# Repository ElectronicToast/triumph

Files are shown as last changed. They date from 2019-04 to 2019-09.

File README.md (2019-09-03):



  

Analog function generator project for EE 90 at Caltech

## Description

The Triumph Analog Function Generator is an analog function generator constructed for the Analog Electronics Project Laboratory (EE 90) capstone course at Caltech. It provides a single output channel on a 50 Ω impedance matched BNC connector. It is capable of producing sine, square, and triangle waveforms that vary in frequency over at least the range 10 Hz to 20 kHz, in addition to DC. The frequency may be adjusted through the combination of a frequency range select switch and a fine-adjustment knob on the top of the device. The output amplitude may be varied from zero up to 10 V (single-sided)  with a control knob. A second control knob allows the DC offset of the output to be varied. 

Power is supplied via 9 – 18 VDC input through a barrel jack connector on the rear of the device. A rocker switch near the power connector allows the device to be switched on and off.

A blue indicator LED on the front of the device indicates if the function generator is powered.

## Photos

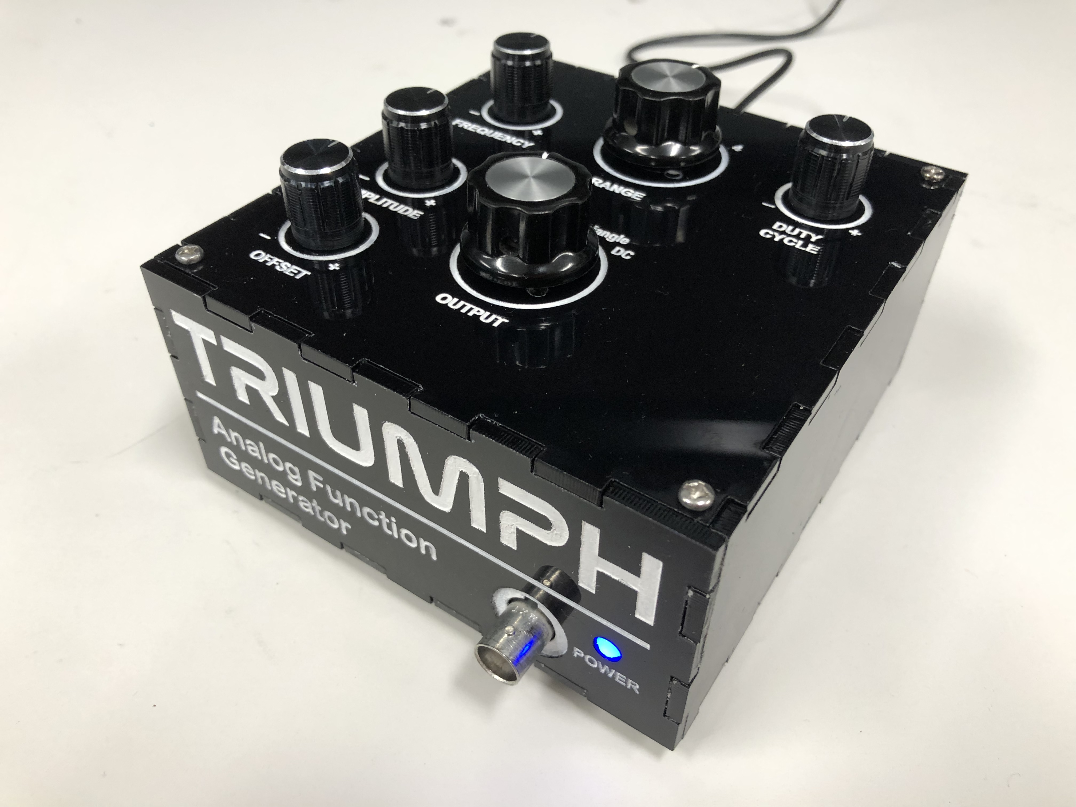
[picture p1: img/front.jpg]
front

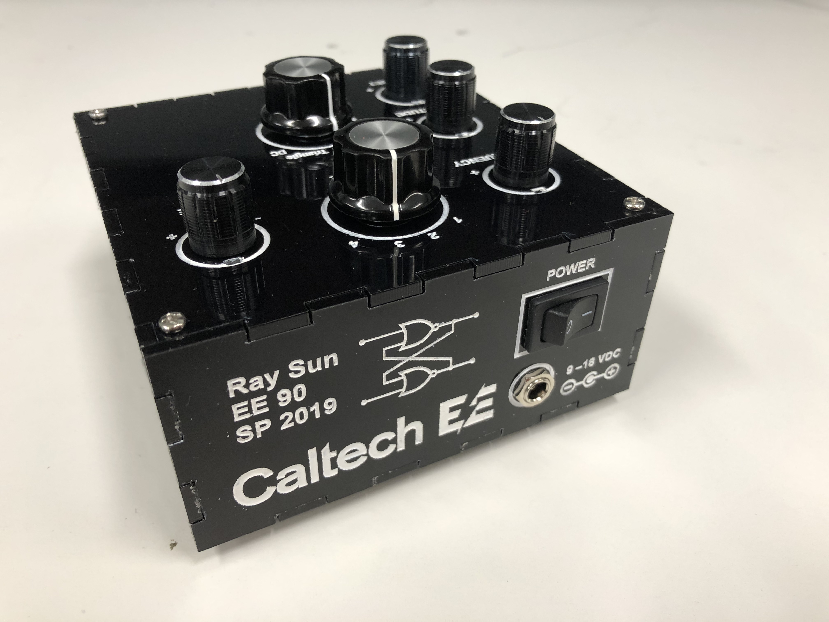
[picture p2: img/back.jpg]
back

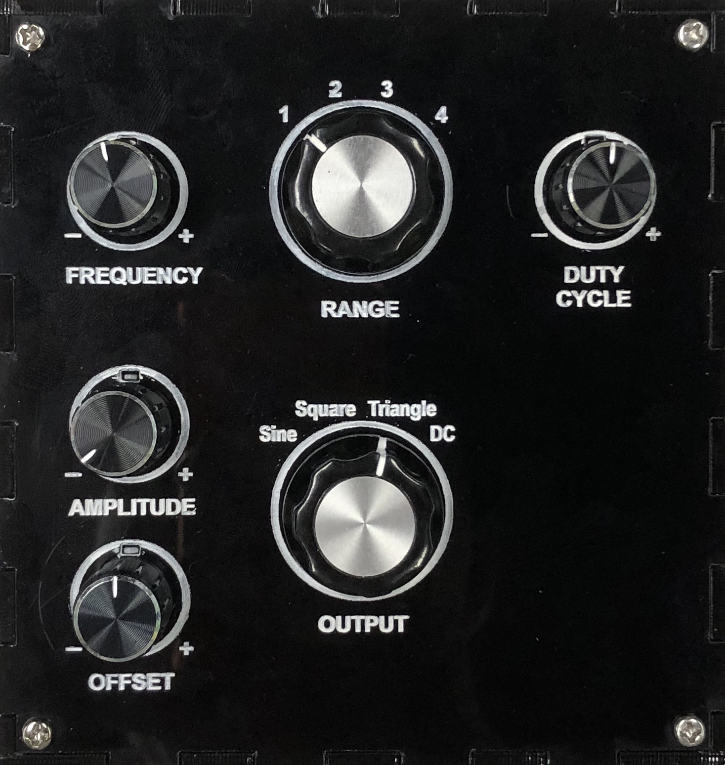
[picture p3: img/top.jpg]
top

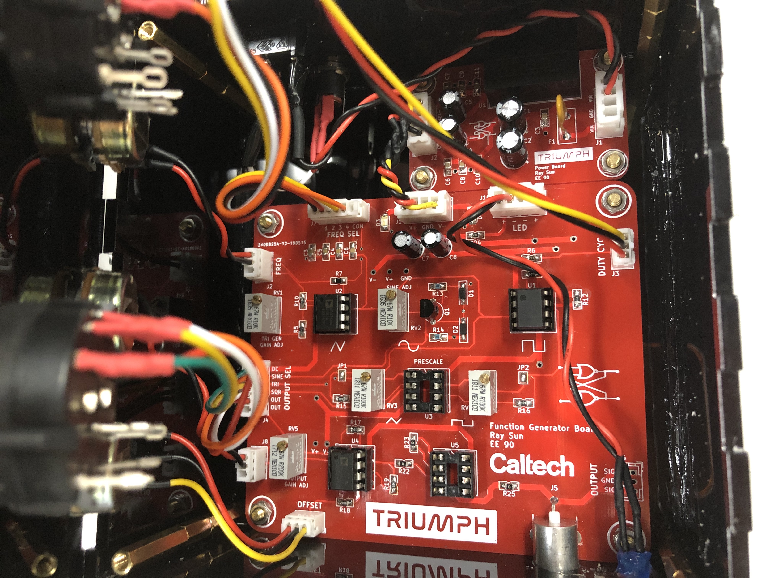
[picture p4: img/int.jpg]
int


## Design

An integrator with Schmitt feedback is used to generate a base triangle wave, which is passed to a Middlebrook-Richer JFET converter to create a sine wave and also a comparator to create a square wave. A positive feedback circuit associated to the comparator provides square wave duty cycle control. A final output stage provides amplitude and offset control. This general architecture achieves a good balance among simplicity, reliability, and performance.

The electronics were split among two PCBs: a main board with the function generator circuitry, and a power board that functions as a DC-DC converter supplying the former with a dual polarity power supply.

The electronics were designed with KiCad EDA v. 5.1.2. The `/triumph-main` directory contains files, documentation, and fabrication output for the main board, while the `/triumph-main-production` directory contains files reflecting post-fabrication design changes. The `/triumph-power` directory contains files for the power board.

The enclosure was designed with SolidWorks 2018, CorelDraw X7, and the [MakerCase](https://en.makercase.com/) box generator.

## Author
- Ray Sun - Undergraduate, Electrical Engineering, Caltech, Class of 2020

## Licensing
This project is released under the terms of the MIT License.

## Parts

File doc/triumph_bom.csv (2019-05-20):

Date | 5/19/2019
Power Board:
Component Count: | 15
Ref | Qnty | Value | Cmp name | Footprint | Description | Vendor
C2, C1, | 2 | 47uF | CP_Small | Capacitor_THT:CP_Radial_D6.3mm_P2.50mm | Polarized capacitor, small symbol | In House
C4, C5, | 2 | 10uF | CP_Small | Capacitor_THT:CP_Radial_D5.0mm_P2.00mm | Polarized capacitor, small symbol | In House
C6, C7, | 2 | 1uF | C_Small | triumph:0805_C_HandSoldering | Unpolarized capacitor, small symbol | Arrow
C8, C9, C3, | 3 | 0.1uF | C_Small | triumph:0805_C_HandSoldering | Unpolarized capacitor, small symbol | Arrow
C10, C11, | 2 | 0.01uF | C_Small | triumph:0805_C_HandSoldering | Unpolarized capacitor, small symbol | Arrow
F1, | 1 | MF-R050 | Polyfuse_Small | Fuse:Fuse_Littelfuse_395Series | Resettable fuse, polymeric positive temperature coefficient, small symbol | Arrow
J2, J1, | 2 | JST_XH_vert_01x04 | Conn_01x04 | Connector_JST:JST_XH_B4B-XH-A_1x04_P2.50mm_Vertical | Generic connector, single row, 01x04, script generated (kicad-library-utils/schlib/autogen/connector/) | In House
U1, | 1 | RS-1212D | RS-1212D | triumph:RS-xxxxD | Dual +/-12V Regulated Converter | In House
Main Board:
Component Count: | 78
Ref | Qnty | Value | Cmp name | Footprint | Description | Vendor
C3, C22, C26, C19, C23, | 5 | 10uF | C_Small | triumph:0805_C_HandSoldering | Unpolarized capacitor, small symbol | Arrow
C5, C9, C10, | 3 | 1uF | C_Small | triumph:0805_C_HandSoldering | Unpolarized capacitor, small symbol | Arrow
C7, C8, | 2 | 10uF | CP_Small | Capacitor_THT:CP_Radial_D5.0mm_P2.00mm | Polarized capacitor, small symbol | In House
C15, C16, C6, | 3 | 0.01uF | C_Small | triumph:0805_C_HandSoldering | Unpolarized capacitor, small symbol | Arrow
C21, C20, C24, C25, C2, C1, C14, C13, C18, C17, C4, C11, C12, | 13 | 0.1uF | C_Small | triumph:0805_C_HandSoldering | Unpolarized capacitor, small symbol | Arrow
D2, D1, | 2 | 1N4148 | D_Small_ALT | triumph:D_SOD-123_HandSoldering | Diode, small symbol, filled shape | Arrow
D3, D4, | 2 | LED_B | LED_Small_ALT | triumph:LED_1206_HandSoldering | Light emitting diode, small symbol, filled shape | Arrow
J1, J10, | 2 | JST_XH_vert_01x04 | Conn_01x04 | Connector_JST:JST_XH_B4B-XH-A_1x04_P2.50mm_Vertical | Generic connector, single row, 01x04, script generated (kicad-library-utils/schlib/autogen/connector/) | In House
J4, J7, | 2 | JST_PH_vert_01x06 | Conn_01x06 | Connector_JST:JST_PH_B6B-PH-K_1x06_P2.00mm_Vertical | Generic connector, single row, 01x06, script generated (kicad-library-utils/schlib/autogen/connector/) | In House
J5, | 1 | Molex_73100-0154 | Conn_Coaxial | triumph:Conn_BNC_73100-0154 | coaxial connector (BNC, SMA, SMB, SMC, Cinch/RCA, ...) | Arrow
J9, J8, J3, J2, J6, | 5 | JST_PH_vert_01x03 | Conn_01x03 | Connector_JST:JST_PH_B3B-PH-K_1x03_P2.00mm_Vertical | Generic connector, single row, 01x03, script generated (kicad-library-utils/schlib/autogen/connector/) | In House
JP1, JP2, | 2 | SJ_OPEN | SolderJumper_2_Open | Jumper:SolderJumper-2_P1.3mm_Open_TrianglePad1.0x1.5mm | Solder Jumper, 2-pole, open | N/A
Q1, | 1 | J310 | Q_NJFET_DSG | Package_TO_SOT_THT:TO-92_Inline_Wide | N-JFET transistor, drain/source/gate | In House
R2, R1, R4, R3, R22, R23, | 6 | 0 | R_Small_US | triumph:0805_R_HandSoldering | Resistor, small US symbol | G. G.
R6, | 1 | 1K | R_Small_US | triumph:0805_R_HandSoldering | Resistor, small US symbol | In House
R8, R9, R10, R11, | 4 | 100K | R_Small_US | triumph:0805_R_HandSoldering | Resistor, small US symbol | Arrow
R12, | 1 | 5K | R_Small_US | triumph:0805_R_HandSoldering | Resistor, small US symbol | Arrow
R14, R13, | 2 | 68 | R_Small_US | triumph:0805_R_HandSoldering | Resistor, small US symbol | Arrow
R19, R17, R18, R5, | 4 | 47K | R_Small_US | triumph:0805_R_HandSoldering | Resistor, small US symbol | Arrow
R24, R15, R16, R20, R21, | 5 | 10K | R_Small_US | triumph:0805_R_HandSoldering | Resistor, small US symbol | In House
R25, R7, | 2 | 50 | R_Small_US | triumph:0805_R_HandSoldering | Resistor, small US symbol | Arrow
RV2, RV1, RV3, RV4, | 4 | 10K | R_POT_US | Potentiometer_THT:Potentiometer_Bourns_3296W_Vertical | Potentiometer, US symbol | Arrow
RV5, | 1 | 200K | R_POT_US | Potentiometer_THT:Potentiometer_Bourns_3296W_Vertical | Potentiometer, US symbol | Digi-Key
U1, | 1 | LM211P | LM311 | Package_DIP:DIP-8_W7.62mm_Socket_LongPads | Voltage Comparator, DIP-8/SOIC-8/SSOP-8 | In House
U4, U5, U2, U3, | 4 | AD826 | TL072 | Package_DIP:DIP-8_W7.62mm_Socket_LongPads | Dual Low-Noise JFET-Input Operational Amplifiers, DIP-8/SOIC-8 | In House
N/A | 5 | DIP-8 socket |  |  |  | In House

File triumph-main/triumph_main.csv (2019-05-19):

Source: | C:\Users\Ray\Documents\GitHub\triumph\triumph-main\triumph_main.sch
Date: | 5/19/2019 12:09:50 PM
Tool: | Eeschema (5.1.2)-1
Generator: | C:\Program Files\KiCad\bin\scripting\plugins/bom_csv_grouped_by_value_with_fp.py
Component Count: | 78
Ref | Qnty | Value | Cmp name | Footprint | Description | Vendor
C3, C22, C26, C19, C23, | 5 | 10uF | C_Small | triumph:0805_C_HandSoldering | Unpolarized capacitor, small symbol
C5, C9, C10, | 3 | 1uF | C_Small | triumph:0805_C_HandSoldering | Unpolarized capacitor, small symbol
C7, C8, | 2 | 10uF | CP_Small | Capacitor_THT:CP_Radial_D5.0mm_P2.00mm | Polarized capacitor, small symbol
C15, C16, C6, | 3 | 0.01uF | C_Small | triumph:0805_C_HandSoldering | Unpolarized capacitor, small symbol
C21, C20, C24, C25, C2, C1, C14, C13, C18, C17, C4, C11, C12, | 13 | 0.1uF | C_Small | triumph:0805_C_HandSoldering | Unpolarized capacitor, small symbol
D2, D1, | 2 | 1N4148 | D_Small_ALT | triumph:D_SOD-123_HandSoldering | Diode, small symbol, filled shape
D3, D4, | 2 | LED_B | LED_Small_ALT | triumph:LED_1206_HandSoldering | Light emitting diode, small symbol, filled shape
J1, J10, | 2 | JST_XH_vert_01x04 | Conn_01x04 | Connector_JST:JST_XH_B4B-XH-A_1x04_P2.50mm_Vertical | Generic connector, single row, 01x04, script generated (kicad-library-utils/schlib/autogen/connector/)
J4, J7, | 2 | JST_PH_vert_01x06 | Conn_01x06 | Connector_JST:JST_PH_B6B-PH-K_1x06_P2.00mm_Vertical | Generic connector, single row, 01x06, script generated (kicad-library-utils/schlib/autogen/connector/)
J5, | 1 | Molex_73100-0154 | Conn_Coaxial | triumph:Conn_BNC_73100-0154 | coaxial connector (BNC, SMA, SMB, SMC, Cinch/RCA, ...)
J9, J8, J3, J2, J6, | 5 | JST_PH_vert_01x03 | Conn_01x03 | Connector_JST:JST_PH_B3B-PH-K_1x03_P2.00mm_Vertical | Generic connector, single row, 01x03, script generated (kicad-library-utils/schlib/autogen/connector/)
JP1, JP2, | 2 | SJ_OPEN | SolderJumper_2_Open | Jumper:SolderJumper-2_P1.3mm_Open_TrianglePad1.0x1.5mm | Solder Jumper, 2-pole, open
Q1, | 1 | J310 | Q_NJFET_DSG | Package_TO_SOT_THT:TO-92_Inline_Wide | N-JFET transistor, drain/source/gate
R2, R1, R4, R3, R22, R23, | 6 | 0 | R_Small_US | triumph:0805_R_HandSoldering | Resistor, small US symbol
R6, | 1 | 1K | R_Small_US | triumph:0805_R_HandSoldering | Resistor, small US symbol
R8, R9, R10, R11, | 4 | 100K | R_Small_US | triumph:0805_R_HandSoldering | Resistor, small US symbol
R12, | 1 | 5K | R_Small_US | triumph:0805_R_HandSoldering | Resistor, small US symbol
R14, R13, | 2 | 68 | R_Small_US | triumph:0805_R_HandSoldering | Resistor, small US symbol
R19, R17, R18, R5, | 4 | 47K | R_Small_US | triumph:0805_R_HandSoldering | Resistor, small US symbol
R24, R15, R16, R20, R21, | 5 | 10K | R_Small_US | triumph:0805_R_HandSoldering | Resistor, small US symbol
R25, R7, | 2 | 50 | R_Small_US | triumph:0805_R_HandSoldering | Resistor, small US symbol
RV2, RV1, RV3, RV4, | 4 | 10K | R_POT_US | Potentiometer_THT:Potentiometer_Bourns_3296W_Vertical | Potentiometer, US symbol
RV5, | 1 | 200K | R_POT_US | Potentiometer_THT:Potentiometer_Bourns_3296W_Vertical | Potentiometer, US symbol
U1, | 1 | LM211P | LM311 | Package_DIP:DIP-8_W7.62mm_Socket_LongPads | Voltage Comparator, DIP-8/SOIC-8/SSOP-8
U4, U5, U2, U3, | 4 | AD826 | TL072 | Package_DIP:DIP-8_W7.62mm_Socket_LongPads | Dual Low-Noise JFET-Input Operational Amplifiers, DIP-8/SOIC-8

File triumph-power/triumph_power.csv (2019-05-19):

Source: | C:\Users\Ray\Documents\GitHub\triumph\triumph-power\triumph_power.sch
Date: | 5/19/2019 12:16:21 PM
Tool: | Eeschema (5.1.2)-1
Generator: | C:\Program Files\KiCad\bin\scripting\plugins/bom_csv_grouped_by_value_with_fp.py
Component Count: | 15
Ref | Qnty | Value | Cmp name | Footprint | Description | Vendor
C2, C1, | 2 | 47uF | CP_Small | Capacitor_THT:CP_Radial_D6.3mm_P2.50mm | Polarized capacitor, small symbol
C4, C5, | 2 | 10uF | CP_Small | Capacitor_THT:CP_Radial_D5.0mm_P2.00mm | Polarized capacitor, small symbol
C6, C7, | 2 | 1uF | C_Small | triumph:0805_C_HandSoldering | Unpolarized capacitor, small symbol
C8, C9, C3, | 3 | 0.1uF | C_Small | triumph:0805_C_HandSoldering | Unpolarized capacitor, small symbol
C10, C11, | 2 | 0.01uF | C_Small | triumph:0805_C_HandSoldering | Unpolarized capacitor, small symbol
F1, | 1 | MF-R050 | Polyfuse_Small | Fuse:Fuse_Littelfuse_395Series | Resettable fuse, polymeric positive temperature coefficient, small symbol
J2, J1, | 2 | JST_XH_vert_01x04 | Conn_01x04 | Connector_JST:JST_XH_B4B-XH-A_1x04_P2.50mm_Vertical | Generic connector, single row, 01x04, script generated (kicad-library-utils/schlib/autogen/connector/)
U1, | 1 | RS-1212D | RS-1212D | triumph:RS-xxxxD | Dual +/-12V Regulated Converter

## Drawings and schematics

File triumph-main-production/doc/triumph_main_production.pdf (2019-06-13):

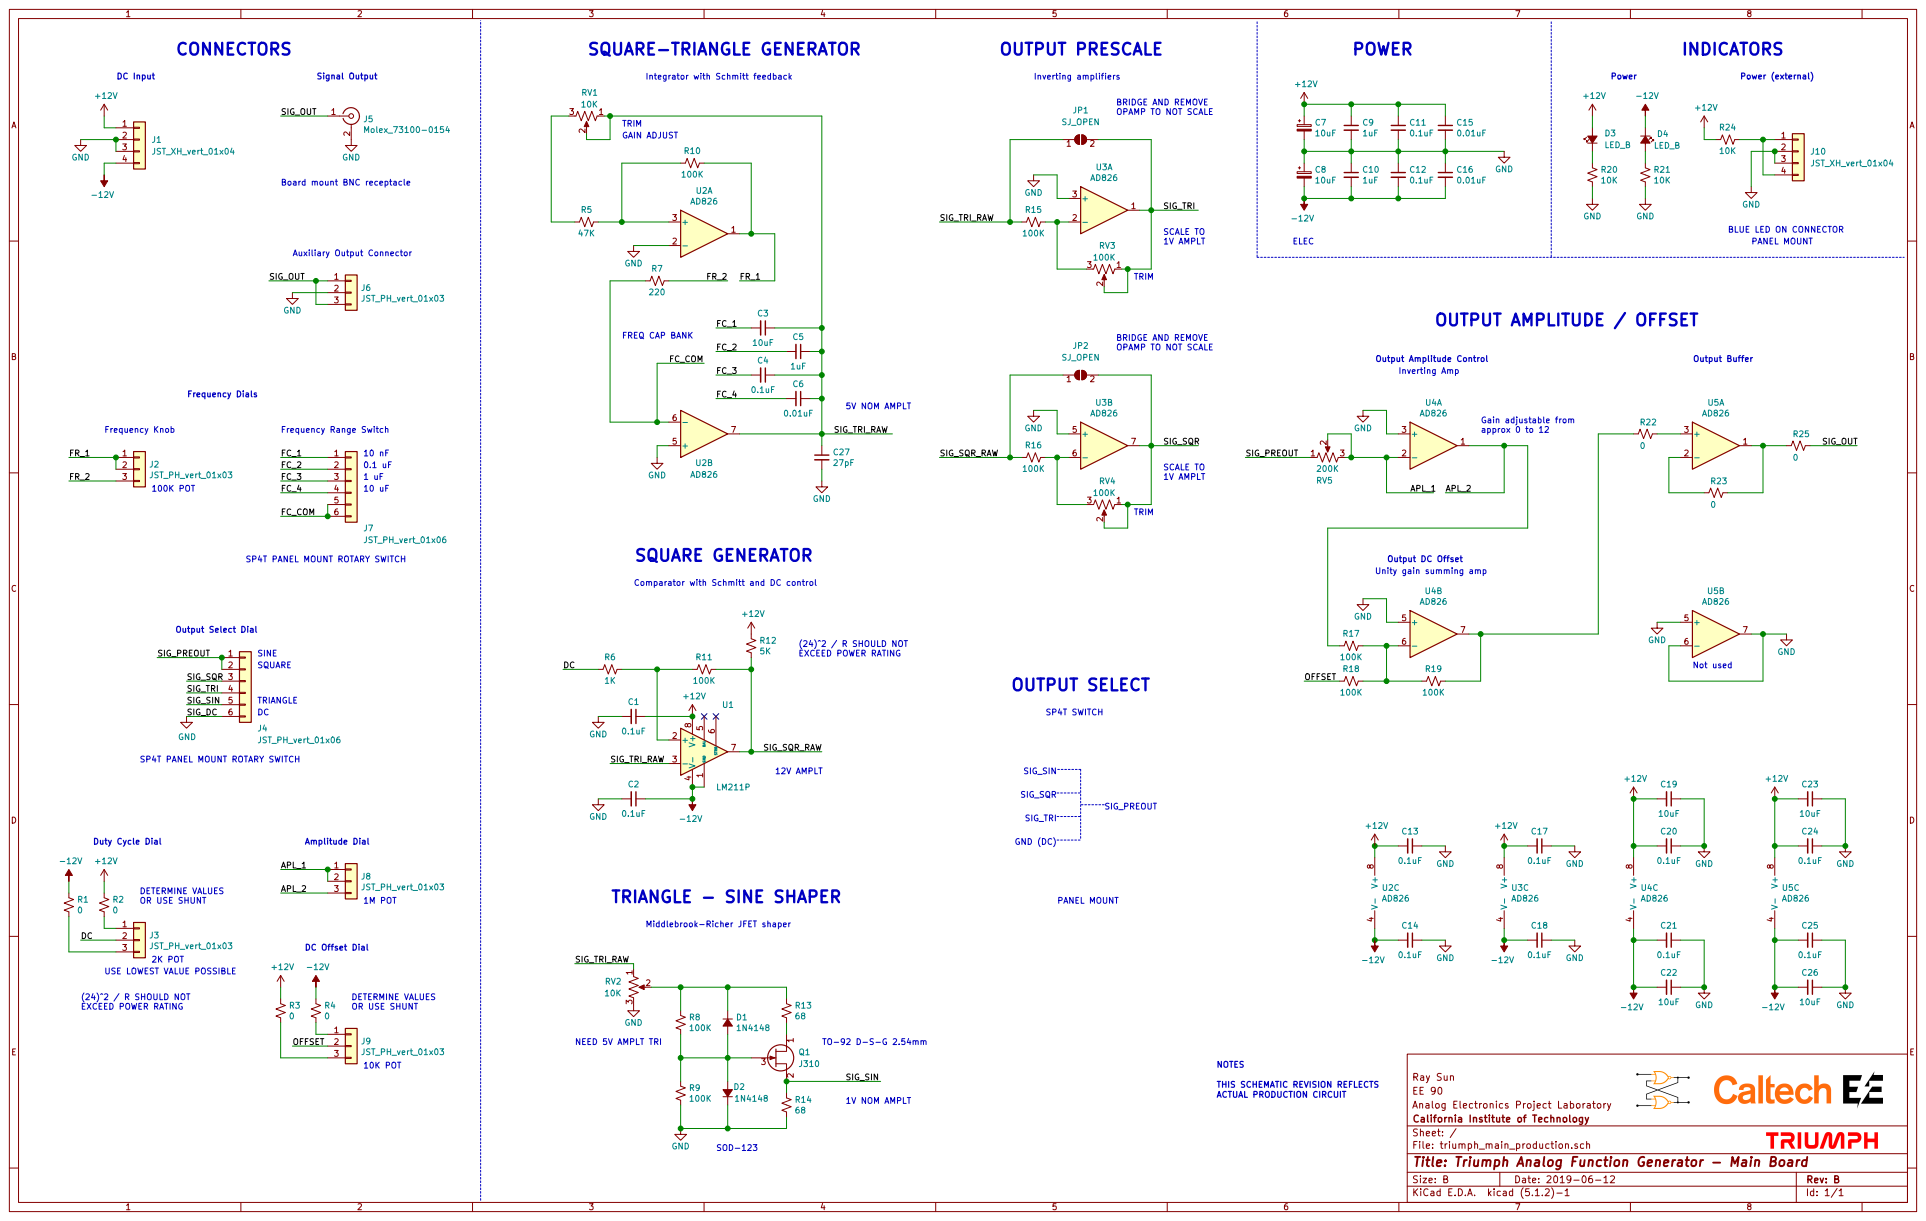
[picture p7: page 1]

Integrator with Schmitt feedback

BRIDGE AND REMOVE OPAMP TO NOT SCALE

Board mount BNC receptacle

BLUE LED ON CONNECTOR

JST_PH_vert_01x03 Auxiliary Output Connector SIG_OUT GND

JST_PH_vert_01x06 Frequency Range Switch FC_1 FC_2 SP4T PANEL MOUNT ROTARY SWITCH

Unity gain summing amp SIG_PREOUT SIG_SIN
AD826 OUTPUT SELECT
PANEL MOUNT SP4T SWITCH

Comparator with Schmitt and DC control

(24)^2 / R SHOULD NOT EXCEED POWER RATING

DETERMINE VALUES OR USE SHUNT

THIS SCHEMATIC REVISION REFLECTS ACTUAL PRODUCTION CIRCUIT

Analog Electronics Project Laboratory EE 90 Ray Sun

File: triumph_main_production.sch Sheet: / California Institute of Technology

Id: 1/1 Title: Triumph Analog Function Generator - Main Board

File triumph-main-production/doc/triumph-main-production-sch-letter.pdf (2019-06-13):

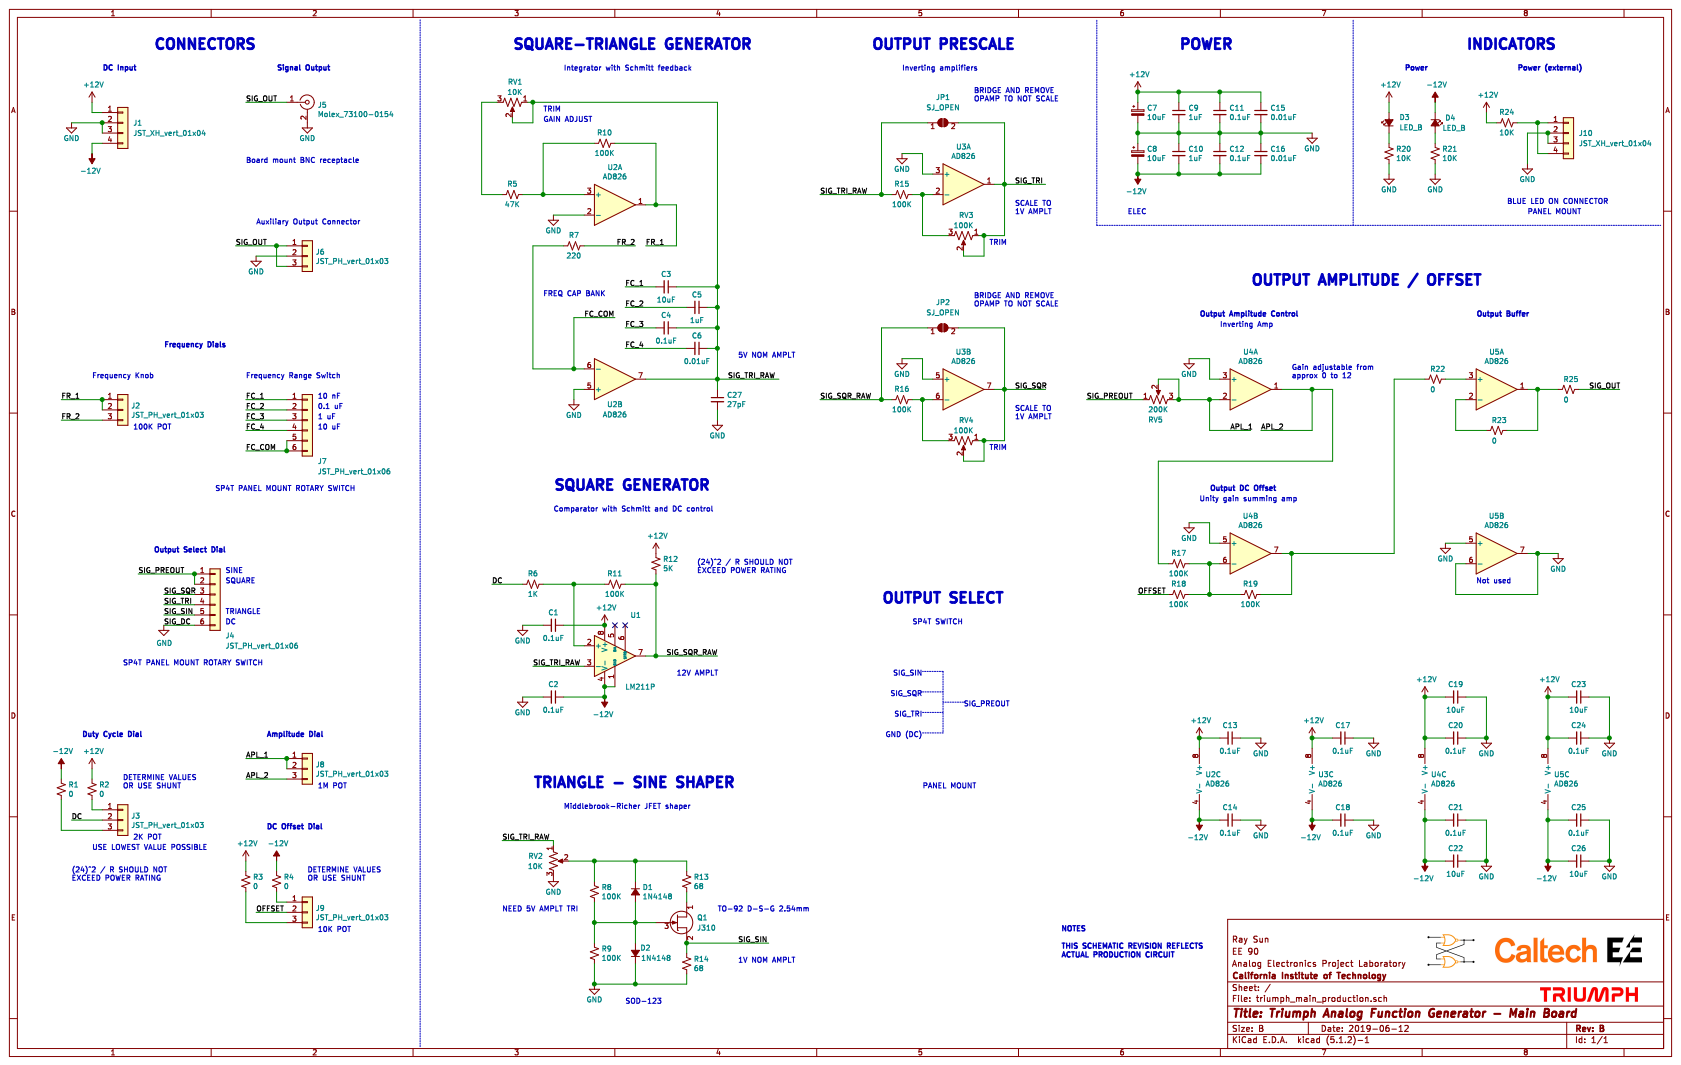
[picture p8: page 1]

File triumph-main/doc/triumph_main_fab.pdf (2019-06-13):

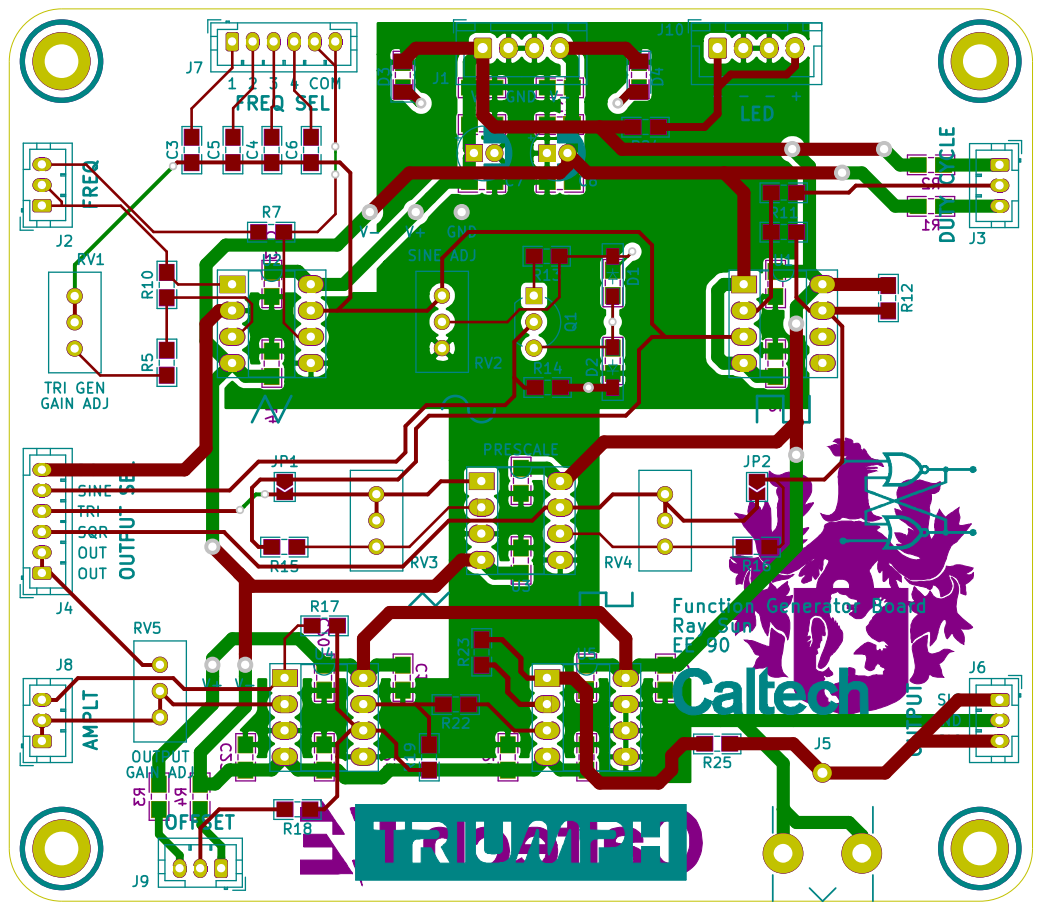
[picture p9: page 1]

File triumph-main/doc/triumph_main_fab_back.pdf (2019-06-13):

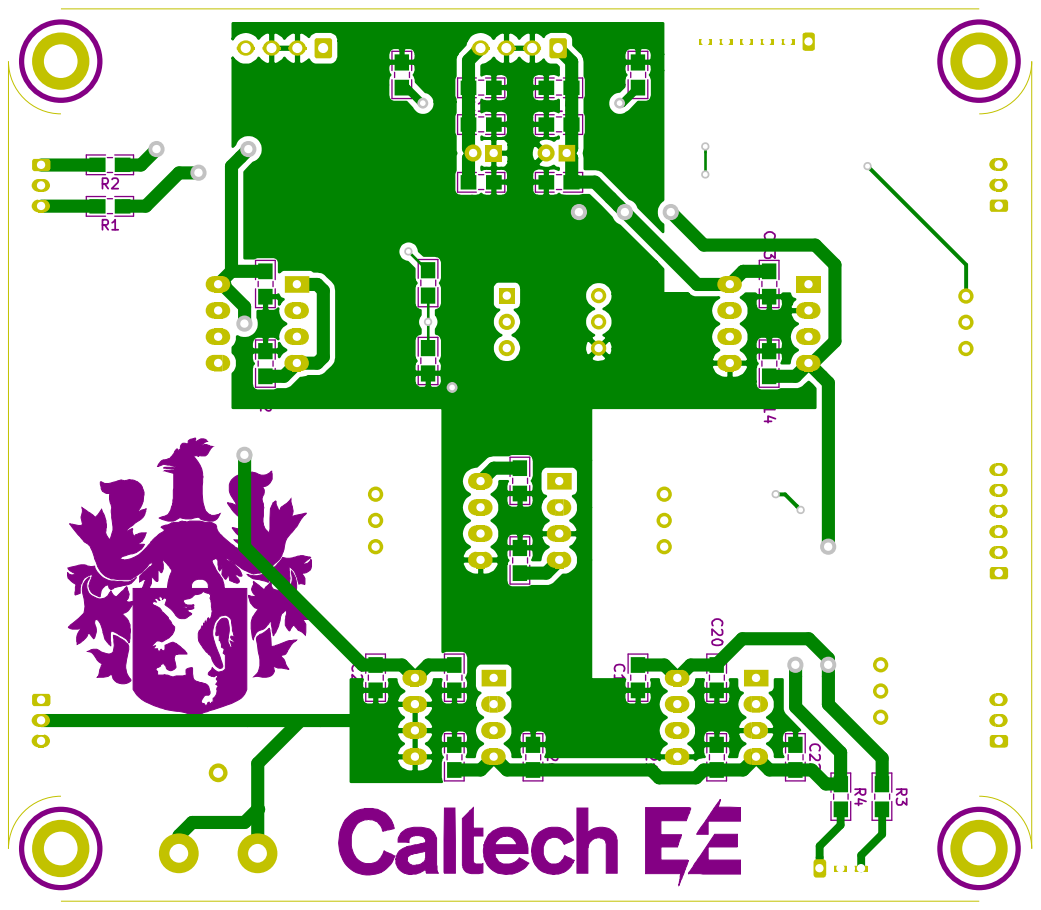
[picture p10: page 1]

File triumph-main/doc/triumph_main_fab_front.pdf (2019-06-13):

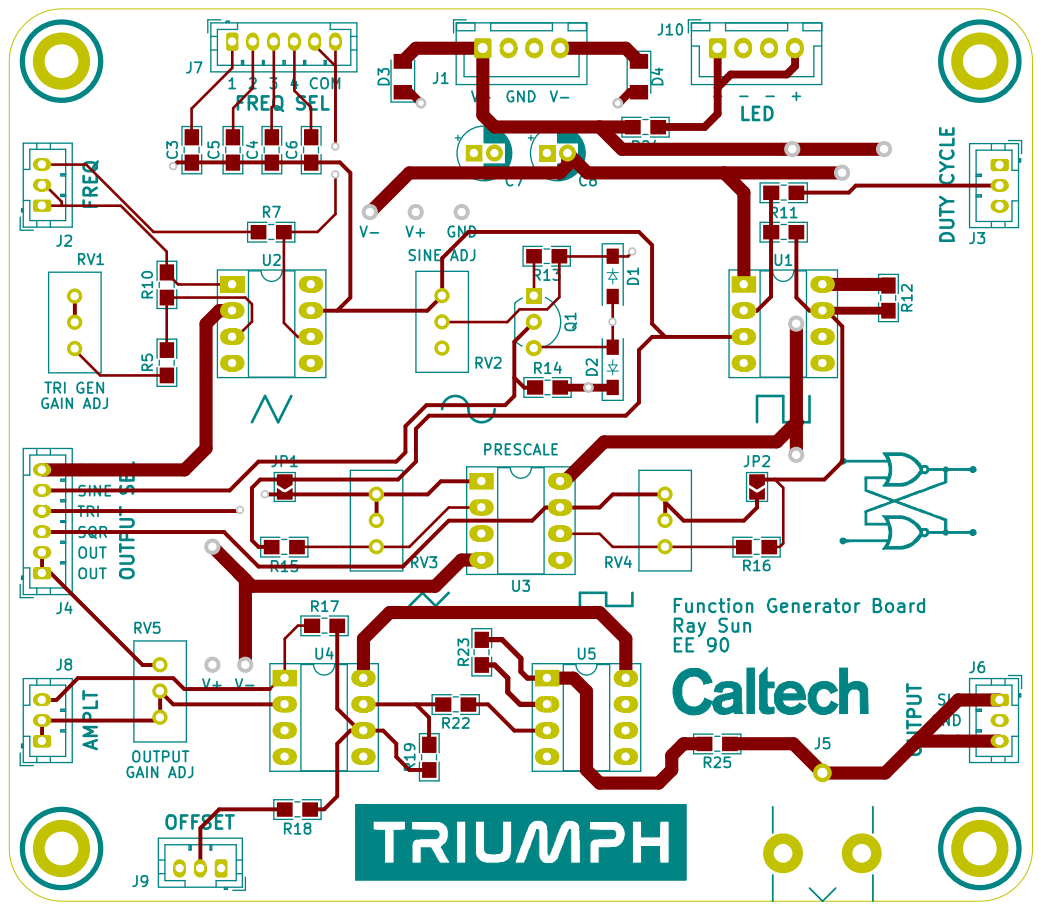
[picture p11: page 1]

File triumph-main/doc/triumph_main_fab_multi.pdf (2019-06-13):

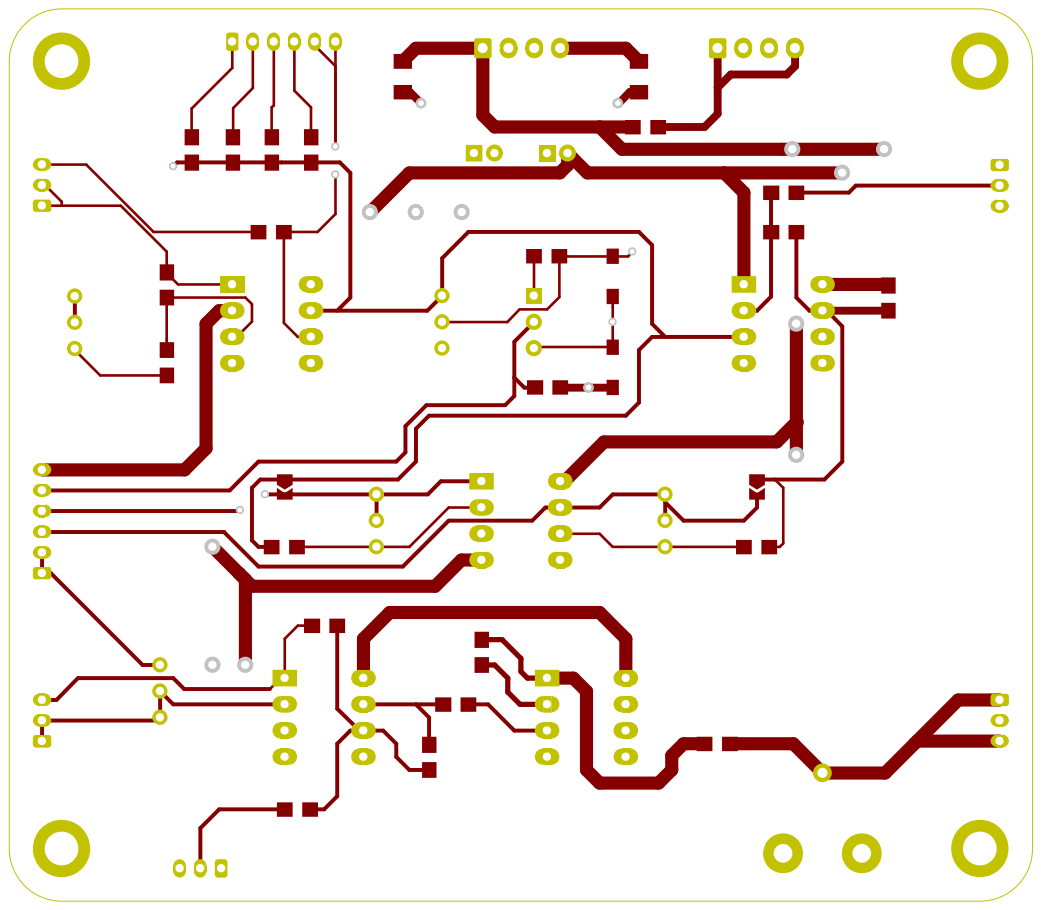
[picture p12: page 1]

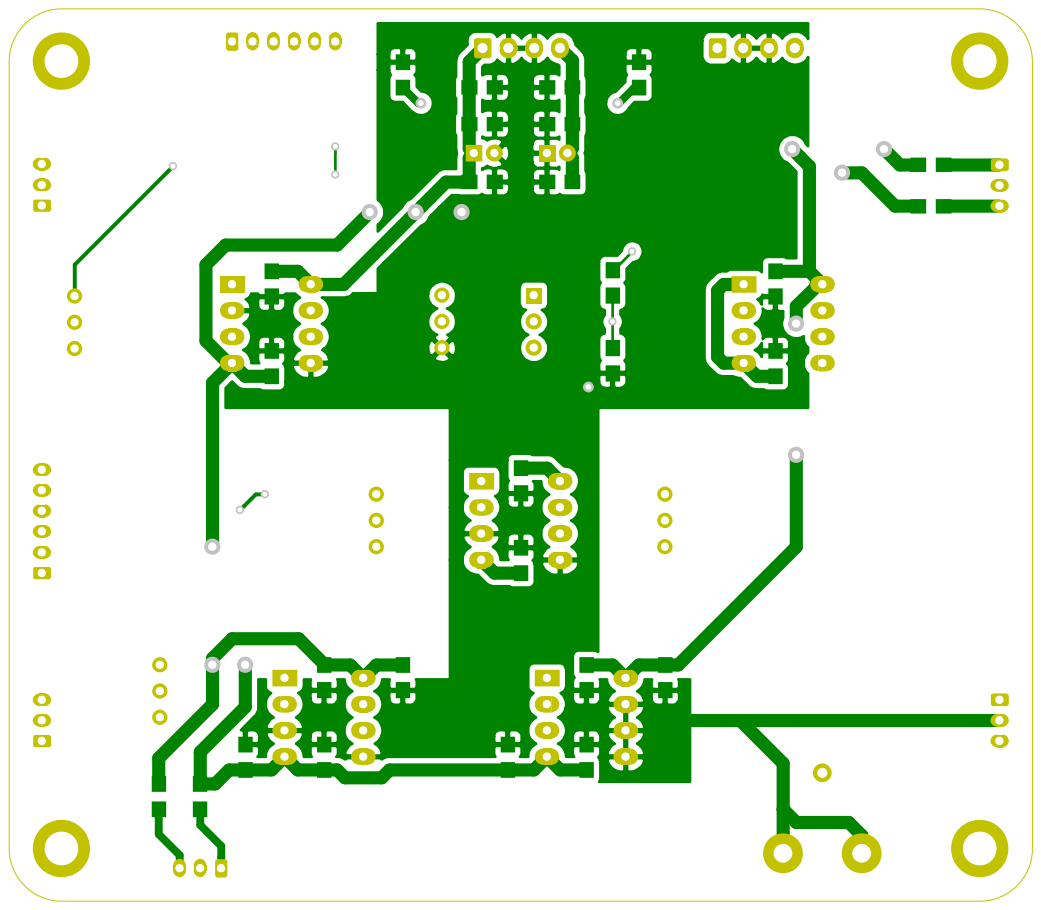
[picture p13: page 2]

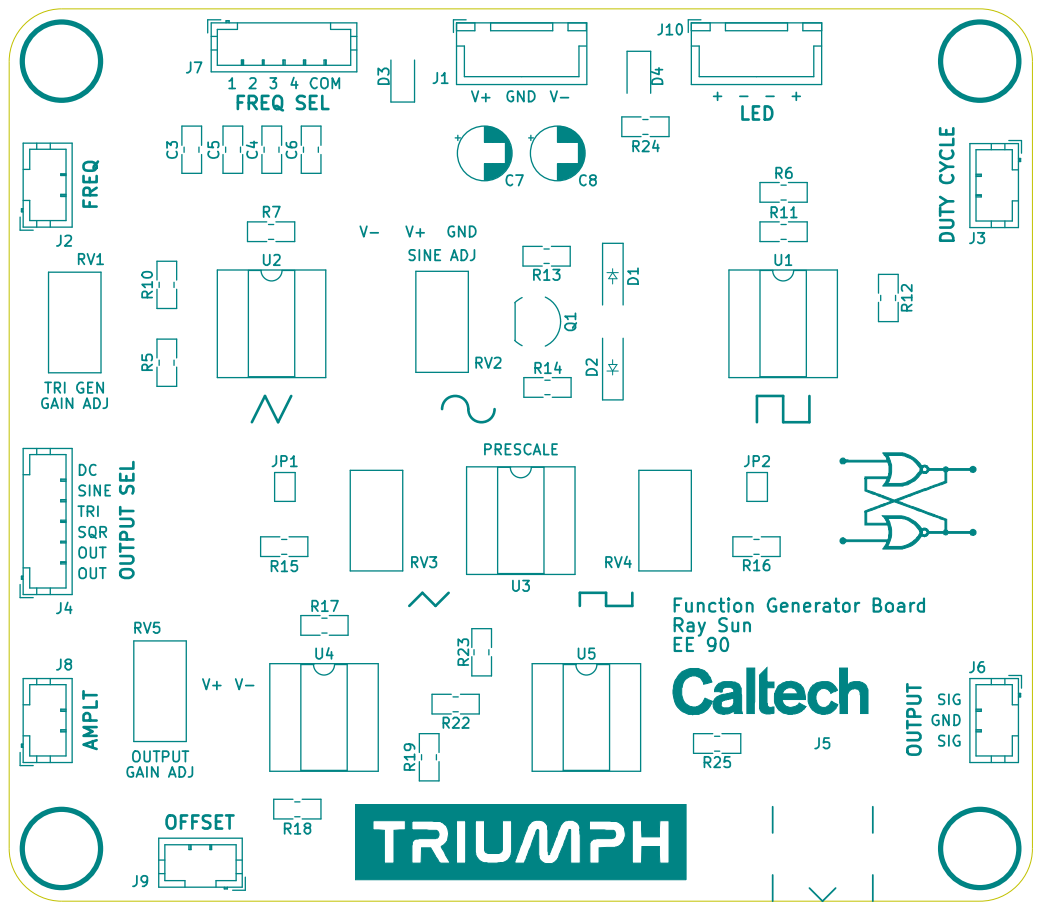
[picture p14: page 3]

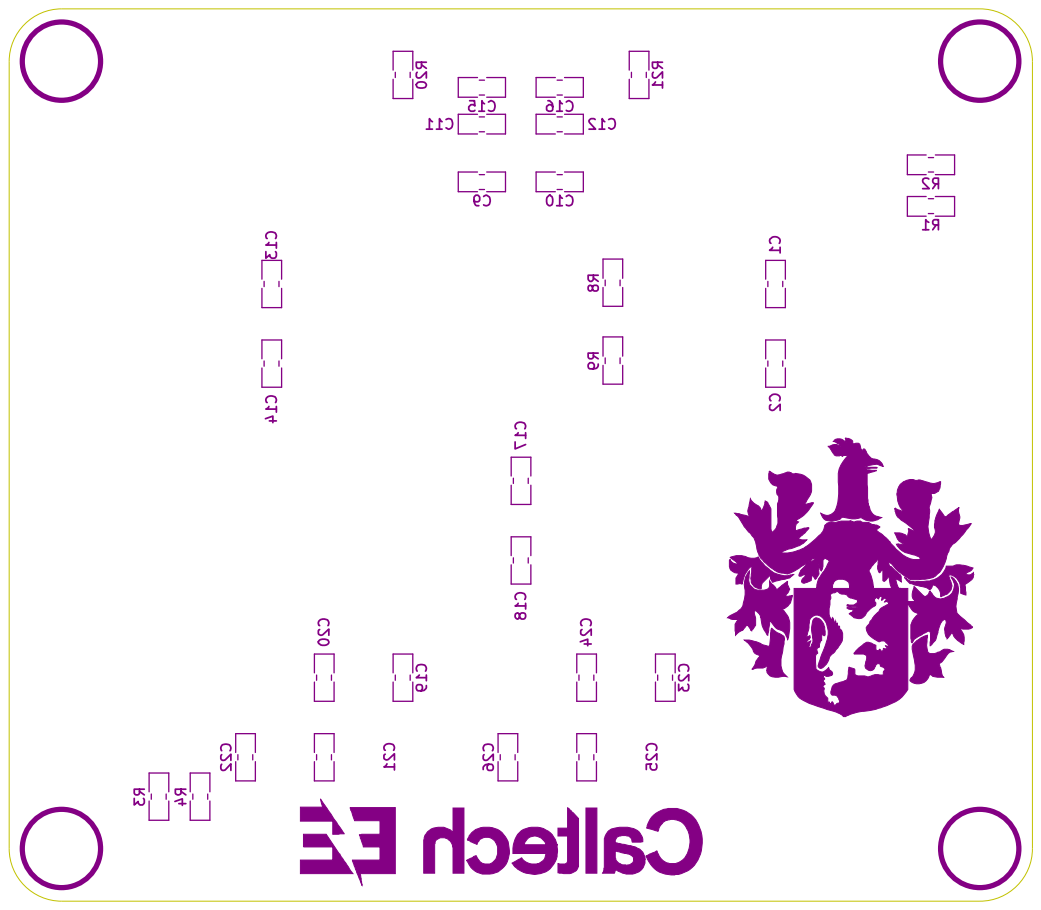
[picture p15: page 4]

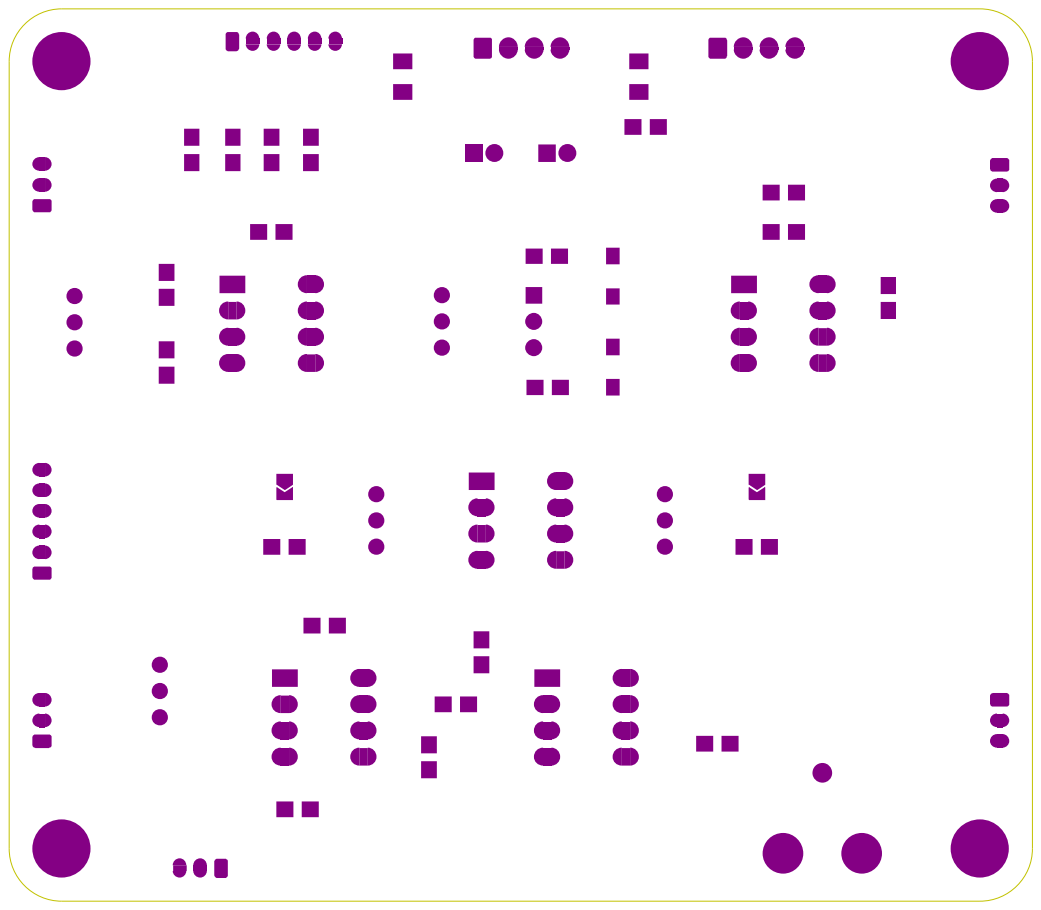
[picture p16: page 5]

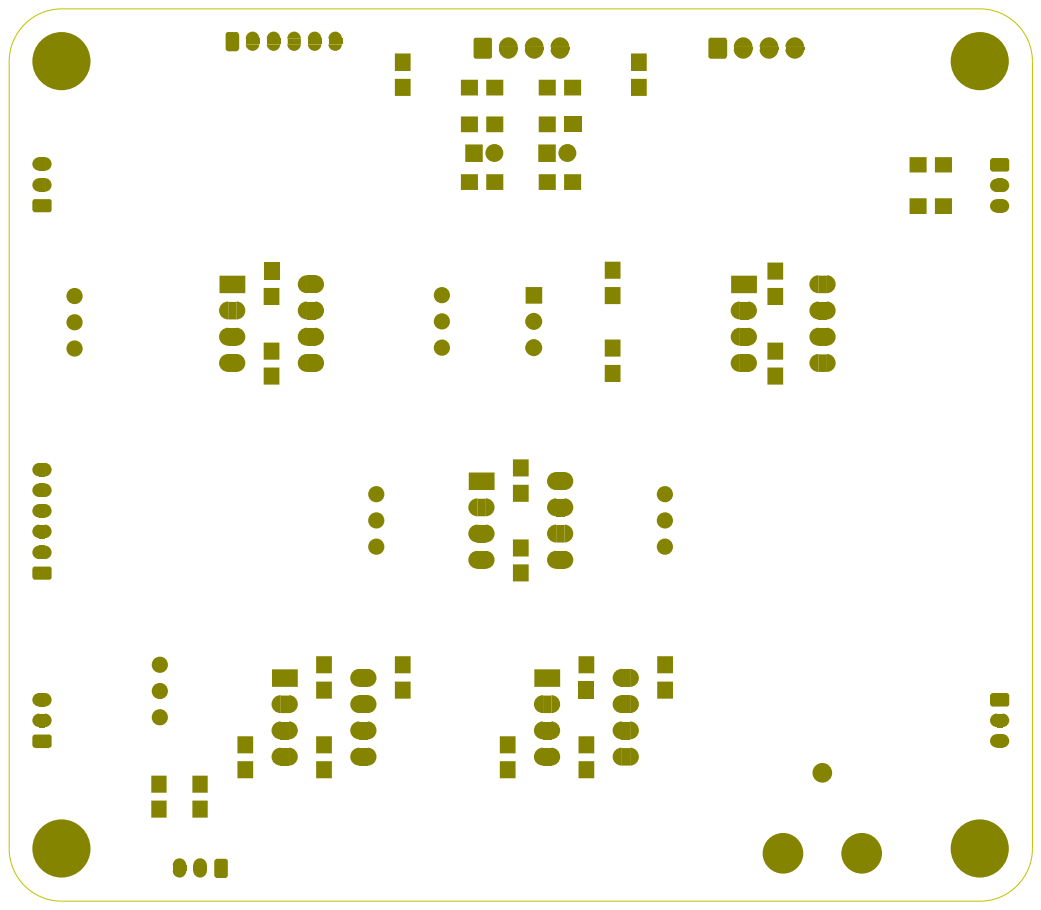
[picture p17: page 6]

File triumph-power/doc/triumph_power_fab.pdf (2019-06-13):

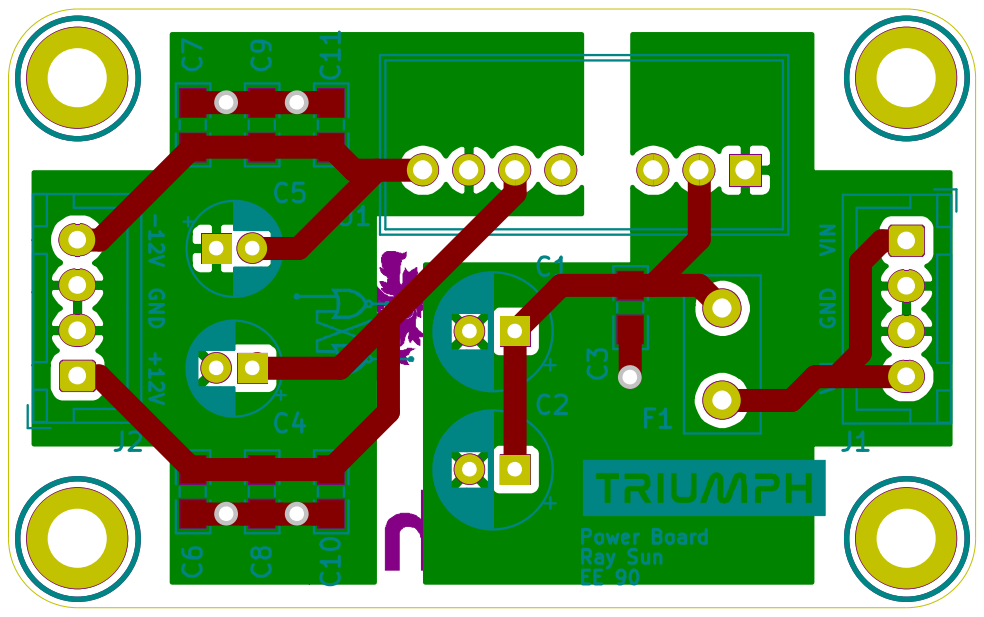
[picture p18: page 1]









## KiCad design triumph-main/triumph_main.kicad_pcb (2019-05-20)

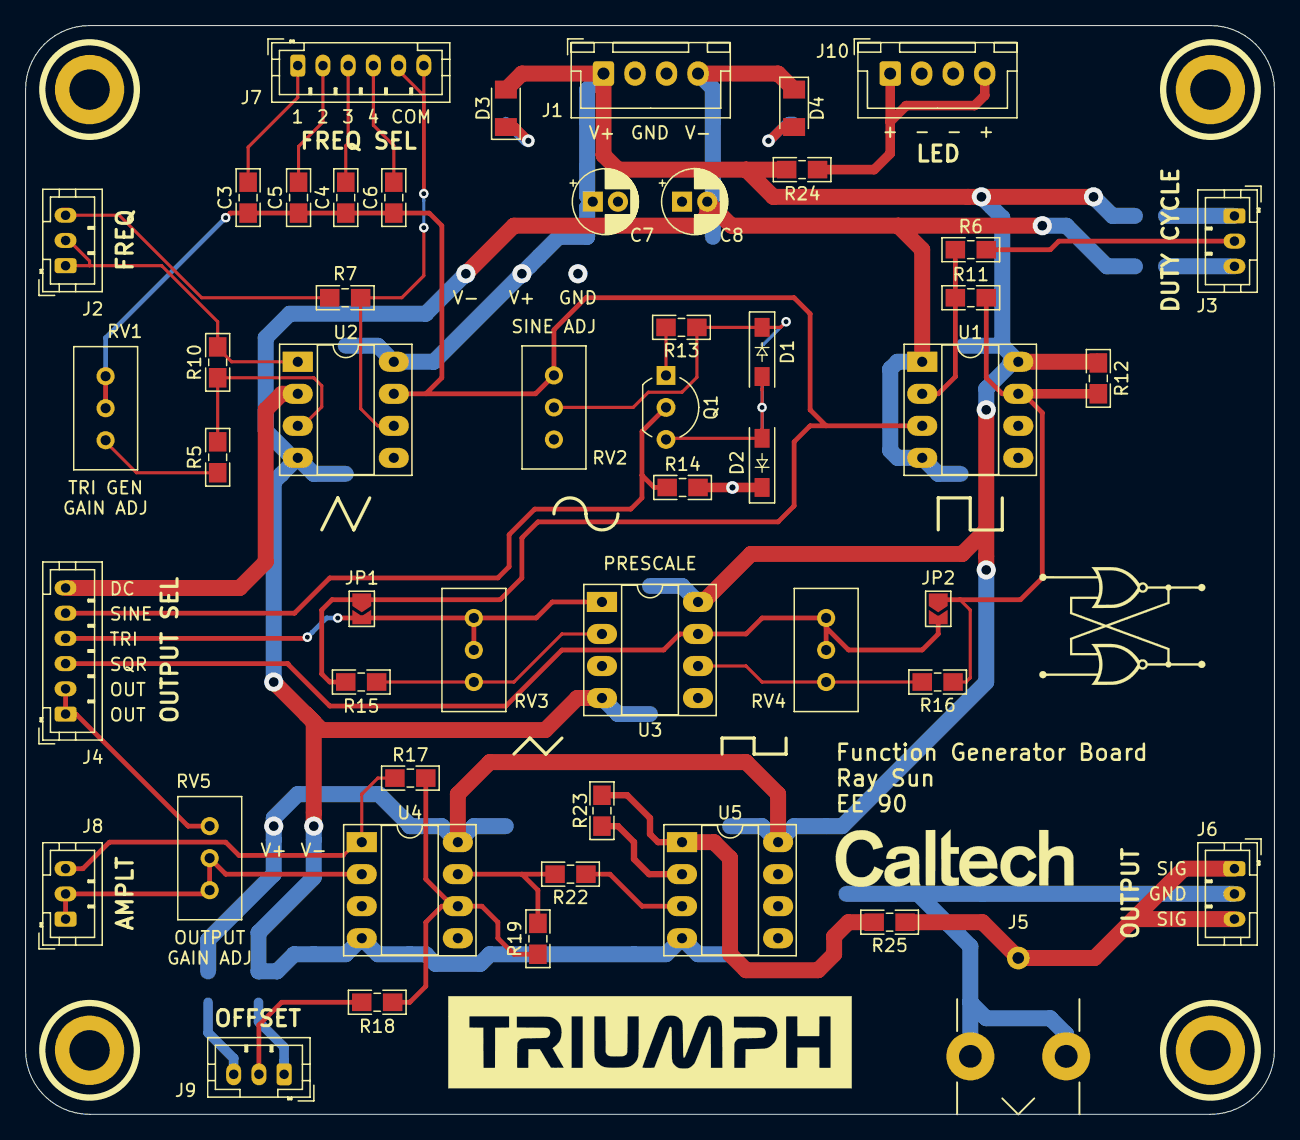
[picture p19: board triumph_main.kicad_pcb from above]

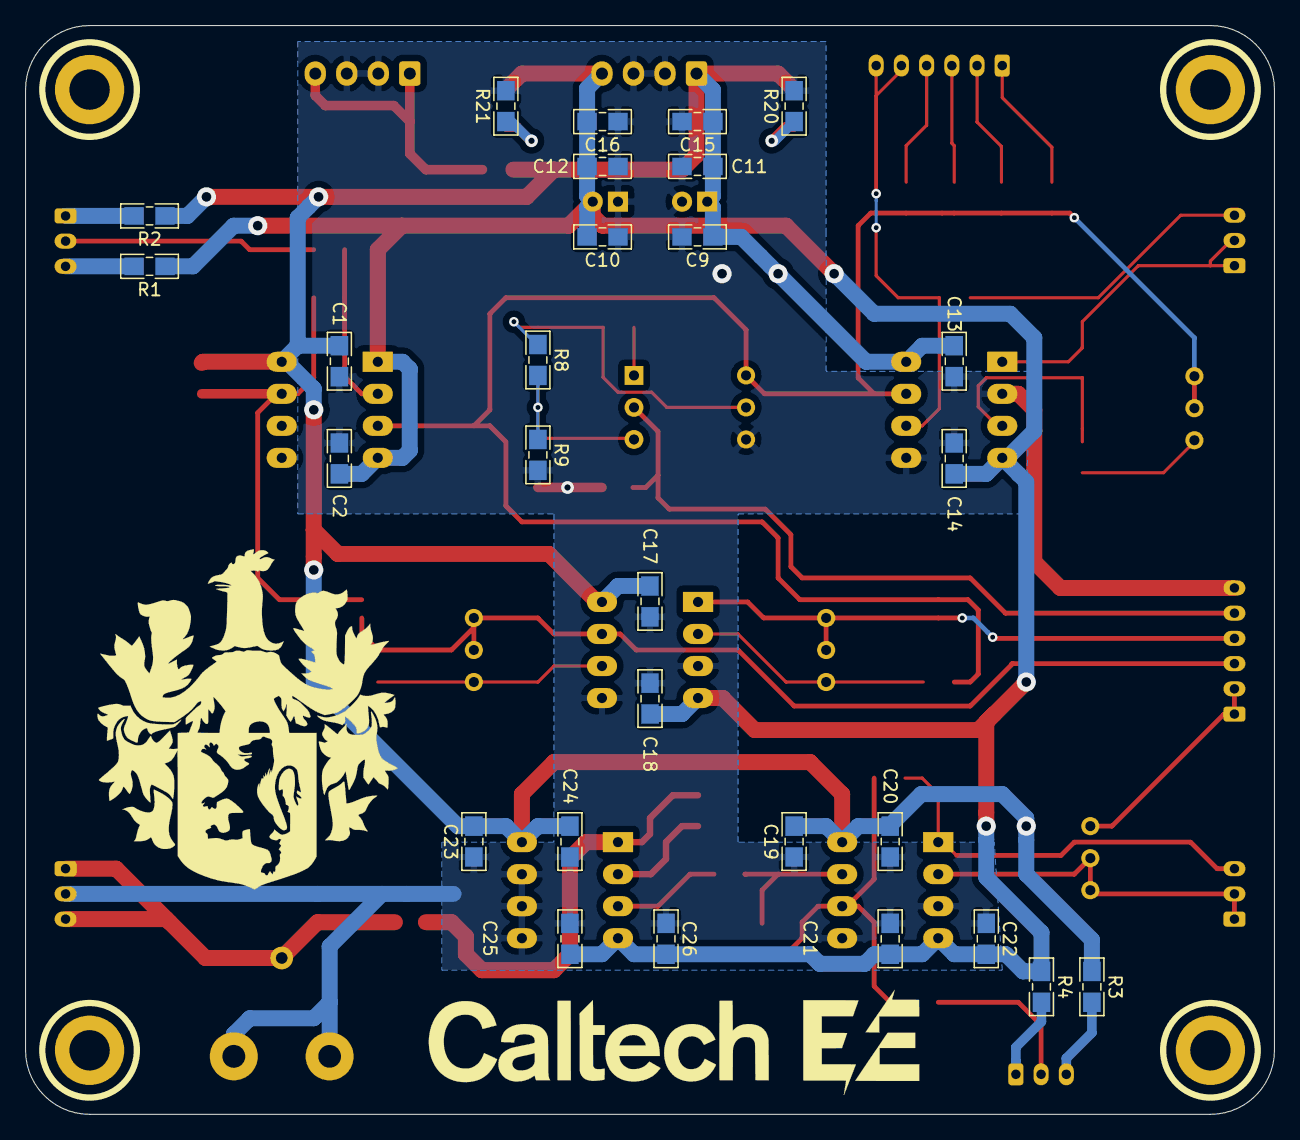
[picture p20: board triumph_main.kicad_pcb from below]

Board: 2 copper layers, 99.1 x 86.4 mm, 78 parts (28 on the bottom side), 41 nets.

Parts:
C1, C2, C4, C11, C12, C13, C14, C17, C18, C20, C21, C24, C25: 0.1uF; 0805_C_HandSoldering
C3, C19, C22, C23, C26: 10uF; 0805_C_HandSoldering
C5, C9, C10: 1uF; 0805_C_HandSoldering
C6: 10nF; 0805_C_HandSoldering
C7, C8: 10uF; CP_Radial_D5.0mm_P2.00mm
C15, C16: 0.01uF; 0805_C_HandSoldering
D1, D2: 1N4148; D_SOD-123_HandSoldering
D3, D4: BLUE; LED_1206_HandSoldering
J1, J10: JST_XH_vert_01x04; JST_XH_B4B-XH-A_1x04_P2.50mm_Vertical
J2, J3, J6, J8, J9: JST_PH_vert_01x03; JST_PH_B3B-PH-K_1x03_P2.00mm_Vertical
J4, J7: JST_PH_vert_01x06; JST_PH_B6B-PH-K_1x06_P2.00mm_Vertical
J5: Conn_BNC; Conn_BNC_73100-0154
JP1, JP2: SJ_OPEN; SolderJumper-2_P1.3mm_Open_TrianglePad1.0x1.5mm
Q1: J310; TO-92_Inline_Wide
R1, R2, R3, R4, R22, R23: 0; 0805_R_HandSoldering
R5, R17, R18, R19: 47K; 0805_R_HandSoldering
R6: 1K; 0805_R_HandSoldering
R7, R25: 50; 0805_R_HandSoldering
R8, R9, R10, R11: 100K; 0805_R_HandSoldering
R12: 5K; 0805_R_HandSoldering
R13, R14: 68; 0805_R_HandSoldering
R15, R16, R20, R21, R24: 10K; 0805_R_HandSoldering
RV1, RV2, RV3, RV4, RV5: 10K; Potentiometer_Bourns_3296W_Vertical
U1: LM211P; DIP-8_W7.62mm_Socket_LongPads
U2, U3, U4, U5: NE5532AP; DIP-8_W7.62mm_Socket_LongPads

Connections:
+12V: C1.1, C7.1, C9.1, C11.1, C13.2, C15.1, C17.2, C19.2, C20.2, C23.2, C24.2, D3.2, J1.1, R2.1, R3.1, R12.1, R24.1, U1.8, U2.8, U3.8, U4.8, U5.8
-12V: C2.1, C8.2, C10.2, C12.2, C14.2, C16.2, C18.2, C21.2, C22.2, C25.2, C26.2, D4.1, J1.4, R1.1, R4.1, U1.1, U1.4, U2.4, U3.4, U4.4, U5.4
/APL_1: J8.1, J8.2, RV5.2, RV5.3, U4.2
/APL_2: J8.3, R17.1, U4.1
/DC: J3.2, R6.1
/FC_1: C3.2, J7.1
/FC_2: C5.2, J7.2
/FC_3: C4.2, J7.3
/FC_4: C6.2, J7.4
/FC_COM: J7.5, J7.6, R7.1, U2.6
/FR_1: J2.1, J2.2, R10.2, U2.1
/FR_2: J2.3, R7.2
/OFFSET: J9.2, R18.1
/SIG_OUT: J5.1, J6.1, J6.3, R25.1
/SIG_PREOUT: J4.1, J4.2, RV5.1
/SIG_SIN: J4.5, Q1.2, R14.1
/SIG_SQR: J4.3, JP2.2, RV4.1, RV4.2, U3.7
/SIG_SQR_RAW: JP2.1, R11.2, R12.2, R16.1, U1.7
/SIG_TRI: J4.4, JP1.2, RV3.1, RV3.2, U3.1
/SIG_TRI_RAW: C3.1, C4.1, C5.1, C6.1, JP1.1, R15.1, RV1.1, RV1.2, RV2.1, U1.3, U2.7
GND: C1.2, C2.2, C7.2, C8.1, C9.2, C10.1, C11.2, C12.1, C13.1, C14.1, C15.2, C16.1, C17.1, C18.1, C19.1, C20.1, C21.1, C22.1, C23.1, C24.1, C25.1, C26.1, D2.1, J1.2, J1.3, J4.6, J5.2, J6.2, J10.2, J10.3, R9.2, R14.2, R20.2, R21.2, RV2.3, U2.2, U2.5, U3.3, U3.5, U4.3, U4.5, U5.5, U5.6, U5.7
unnamed: D1.1, R8.1, R13.1, RV2.2
unnamed: D1.2, D2.2, Q1.3, R8.2, R9.1
unnamed: D3.1, R20.1
unnamed: D4.2, R21.1
unnamed: J3.1, R2.2
unnamed: J3.3, R1.2
unnamed: J9.1, R4.2
unnamed: J9.3, R3.2
unnamed: J10.1, J10.4, R24.2
unnamed: Q1.1, R13.2
unnamed: R5.1, RV1.3
unnamed: R5.2, R10.1, U2.3
unnamed: R6.2, R11.1, U1.2
unnamed: R15.2, RV3.3, U3.2
unnamed: R16.2, RV4.3, U3.6
unnamed: R17.2, R18.2, R19.1, U4.6
unnamed: R19.2, R22.2, U4.7
unnamed: R22.1, U5.3
unnamed: R23.1, R25.2, U5.1
unnamed: R23.2, U5.2

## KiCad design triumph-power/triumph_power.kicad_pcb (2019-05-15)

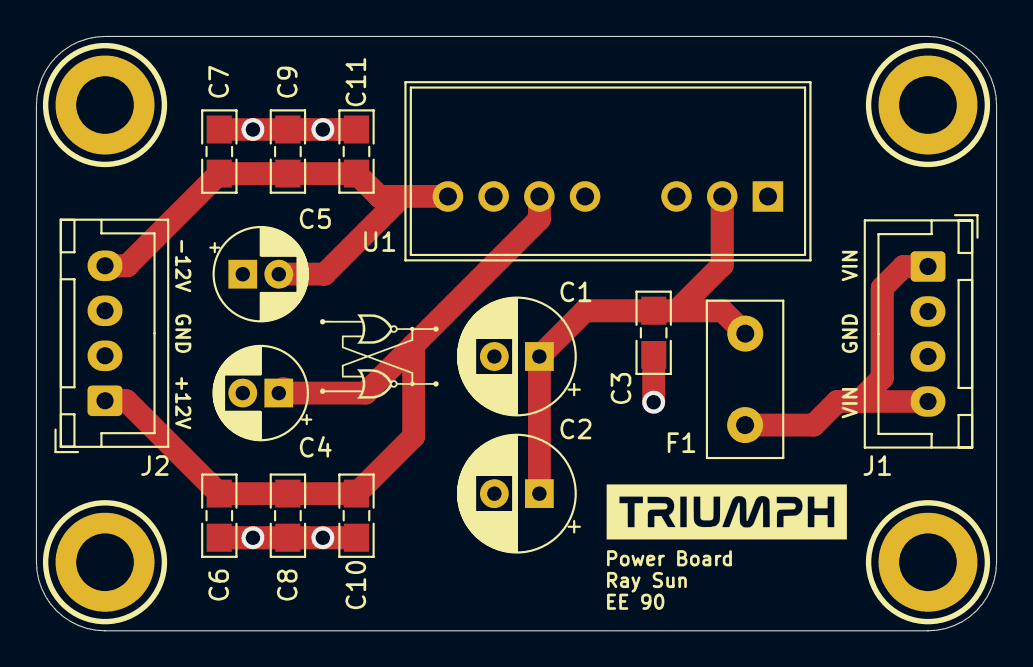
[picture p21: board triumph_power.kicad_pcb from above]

Board: 2 copper layers, 53.3 x 33.0 mm, 15 parts (0 on the bottom side), 6 nets.

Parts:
C1, C2: 47uF; CP_Radial_D6.3mm_P2.50mm
C3, C8, C9: 0.1uF; 0805_C_HandSoldering
C4, C5: 10uF; CP_Radial_D5.0mm_P2.00mm
C6, C7: 1uF; 0805_C_HandSoldering
C10, C11: 0.01uF; 0805_C_HandSoldering
F1: MF-R050; Fuse_Littelfuse_395Series
J1, J2: JST_XH_vert_01x04; JST_XH_B4B-XH-A_1x04_P2.50mm_Vertical
U1: RS-1212D; RS-xxxxD

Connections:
+12V: C4.1, C6.1, C8.1, C10.1, J2.1, U1.6
-12V: C5.2, C7.2, C9.2, C11.2, J2.4, U1.8
GND: C4.2, C5.1, C6.2, C7.1, C8.2, C9.1, C10.2, C11.1, J2.2, J2.3, U1.7
GNDREF: C1.2, C2.2, C3.2, J1.2, J1.3, U1.1
unnamed: C1.1, C2.1, C3.1, F1.2, U1.2
VCC: F1.1, J1.1, J1.4

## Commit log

2019-04-12 Add power board files
    [triumph-power.kicad_pcb, triumph-power.sch]
2019-04-15 Generate main board files
    [triumph-main.kicad_pcb, triumph-main.sch, triumph-power.sch]
2019-04-15 Change to dual transformers
    [triumph-power.sch]
2019-04-17 Add some power components
    [triumph-main.sch]
2019-04-17 Spec potentiometer connectors
    [triumph-main.sch]
2019-04-21 Design output stage
    [triumph-main.sch]
2019-04-22 Complete initial schematic
    [triumph-main.sch]
2019-04-22 Annotate schematic
    [triumph-main.sch]
2019-04-22 Add additional annotation
    [triumph-main.sch]
2019-04-22 Update Wien bridge cap values
    [triumph-main.sch]
2019-04-25 Add title block images
    [triumph-power.sch]
2019-04-25 Fix inane KiCad 5.1.0 labels bug
    [triumph-main.sch]
2019-04-25 Add more input decoupling
    [triumph-main.sch]
2019-04-25 Make schematic version without AC DC converter board
    [triumph.kicad_pcb, triumph.sch]
2019-04-25 Add DC-DC converter
    [triumph.sch]
2019-04-30 Add PTC
    [triumph.sch]
2019-05-02 Migrate to square-triangle generation, sine shaping
    [triumph.sch]
2019-05-02 Make pot pinout standard orientation agnostic
    [triumph.sch]
2019-05-05 Update output matching, Middlebrook
    [triumph.sch]
2019-05-05 Update current wave generation design
    [triumph.sch]
2019-05-05 Remove board LEDs
    [triumph.sch]
2019-05-05 Make output select symmetric
    [triumph.sch]
2019-05-05 Add comparator for DC control
    [triumph.sch]
2019-05-05 Remove protection resistor from gain stage
    [triumph.sch]
2019-05-05 Remove pulldown
    [triumph.sch]
2019-05-05 Update labels
    [triumph.sch]
2019-05-05 Respec power connector
    [triumph.sch]
2019-05-10 Refactor into two separate boards
    [triumph-power.sch, triumph.kicad_pcb, triumph_main.kicad_pcb, triumph_main.sch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]
2019-05-10 Assign 4 pin XH footprint
    [triumph_main.sch, triumph_power.sch]
2019-05-10 Add preliminary power board
    [triumph_power.kicad_pcb, triumph_power.sch]
2019-05-10 Add trimpots and auxiliary power connector
    [triumph_main.sch]
2019-05-11 Add 0 ohm shunts
    [triumph_main.sch]
2019-05-11 Update square generator
    [triumph_main.sch]
2019-05-12 Update to breadboard prototype
    [triumph_main.sch]
2019-05-12 Generate preliminary schematic print
    [triumph_main.sch, triumph_power.sch]
2019-05-12 Route power board
    [triumph_power.kicad_pcb, triumph_power.sch]
2019-05-12 Add a prodigious quantity of PCB graphics
    [triumph_power.kicad_pcb, triumph_power.sch]
2019-05-12 Add alternative PCB based on planes
    [triumph_power_alt.kicad_pcb]
2019-05-12 Replace input resistor on output gain stage with trimpot
    [triumph_main.sch]
2019-05-12 Assign provisional footprints for BNC and tantalum caps
    [triumph_main.sch]
2019-05-12 Replace 0805 footprints with custom ones
    [triumph_main.sch]
2019-05-12 Replace LM211 footprint with DIP8 socket
    [triumph_main.sch]
2019-05-12 Begin layout
    [triumph_main.kicad_pcb]
2019-05-12 Continue placement
    [triumph_main.kicad_pcb]
2019-05-12 Copy schematic for alternative power board
    [triumph_power_alt.sch]
2019-05-13 Generate preliminary documentation
    [triumph_power.sch]
2019-05-13 Remove alternative power board
    [triumph_power_alt.kicad_pcb, triumph_power_alt.sch]
2019-05-13 Add additional power filtering caps and update electrolytic cap footprints
    [triumph_main.sch, triumph_power.sch]
2019-05-13 Reroute power board
    [triumph_power.kicad_pcb, triumph_power.sch]
2019-05-13 Generate gerbers
    [triumph_power-B_Cu.gbl, triumph_power-B_Mask.gbs, triumph_power-B_Paste.gbp, triumph_power-B_SilkS.gbo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]
2019-05-13 Remove paste gerbers
    [triumph_power-B_Cu.gbl, triumph_power-B_Mask.gbs, triumph_power-B_Paste.gbp, triumph_power-B_SilkS.gbo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]
2019-05-13 Add board dimension markers
    [triumph_power.kicad_pcb]
2019-05-13 Change dimensions to inches
    [triumph_power.kicad_pcb]
2019-05-13 Add cap bank
    [triumph_main.sch]
2019-05-13 Correct tantalum orientation
    [triumph_main.sch]
2019-05-14 Determine board edge
    [triumph_main.kicad_pcb]
2019-05-14 Determine board outline
    [triumph_main.kicad_pcb]
2019-05-14 Add BNC connector footprint
2019-05-14 Begin routing
    [triumph_main.kicad_pcb, triumph_main.sch]
2019-05-14 Make cosmetic edits
    [triumph_power-B_Cu.gbl, triumph_power-B_Mask.gbs, triumph_power-B_SilkS.gbo, triumph_power-Edge_Cuts.gm1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]
2019-05-14 Add more cosmetics
    [triumph_main.kicad_pcb]
2019-05-14 Finish routing
    [triumph_main.kicad_pcb, triumph_main.sch]
2019-05-14 Add more labels
    [triumph_main.kicad_pcb]
2019-05-14 Add missing conector labels
    [triumph_main.kicad_pcb]
2019-05-14 Make some traces thicker, 50 mil power
    [triumph_main.kicad_pcb]
2019-05-14 Make thicker intermediate signal traces, more labels
    [triumph_main.kicad_pcb, triumph_main.sch]
2019-05-14 Remove via tenting
    [triumph_main-B_Cu.gbl, triumph_main-B_Mask.gbs, triumph_main-B_SilkS.gbo, triumph_main-Edge_Cuts.gm1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]
2019-05-15 Add onboard power LEDs
    [triumph_main-B_Cu.gbl, triumph_main-B_Mask.gbs, triumph_main-B_SilkS.gbo, triumph_main-Edge_Cuts.gm1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]
2019-05-15 Correct triangle wave opamp orientation
    [triumph_main-B_Cu.gbl, triumph_main-B_Mask.gbs, triumph_main-B_SilkS.gbo, triumph_main-Edge_Cuts.gm1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]
2019-05-15 Regenerate pdf
    [triumph_main.sch]
2019-05-15 Generate first version documentation
    [triumph_main.drl, triumph_main.kicad_pcb, triumph_power.drl, triumph_power.kicad_pcb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]
2019-05-15 Remove drill files from documentation
    [triumph_main.drl, triumph_power.drl]
2019-05-19 Edit some component fields to reflect values for production
    [triumph_main.sch]
2019-05-19 Generate letter size fabrication schematic and BOMs
    [triumph_main.csv, triumph_power.csv]
2019-05-19 Make combined BOM
    [triumph_bom.csv]
2019-05-20 Order parts
    [triumph_bom.csv, triumph_main.kicad_pcb, triumph_main.sch]
2019-06-03 Add schematic to represent actual production values used
    [triumph_main_production.sch]
2019-06-13 Add more documentation
    [triumph_main_production.sch]
2019-06-13 Add enclosure fabrication file
